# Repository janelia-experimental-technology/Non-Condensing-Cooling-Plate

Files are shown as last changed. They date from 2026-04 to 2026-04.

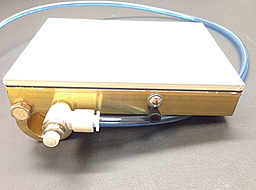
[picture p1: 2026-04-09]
Non-Condensing-Cooling-Plate.png

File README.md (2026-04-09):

### Non-condensing cooling plate

Cooling plates are common in the scientific environment. However, depending on the humidity of the environment, the cold surface of the cooling plate can cause moisture in the air to condense on the surface, thus interfering with certain tasks. For example, if using a cooling plate while sorting fruit flies, excess moisture on the plate may cause flies to drown.

Inventors at Howard Hughes Medical Institute’s Janelia Research Campus have designed a cooling plate that keeps the working surface completely dry and cool, independent of the working environment’s conditions. This is achieved by cooling/drying air and forcing it through a porous stainless steel plate. Instead of water condensing on top of the surface, water is allowed to condense inside the device (below the surface) and is forced out by air pressure through a drain. The airflow is gentle enough not to disturb the work surface, but enough to prevent condensation.

Compressed lab air, a chilled water supply, and peltier with controller are required for this technology. The current configuration is designed for fruit fly sorting and thus has an integrated vial chiller to pre-chill the flies before they are sorted. A variety of vial sizes can be accommodated to the existing design via vial adapters. A variety of fittings can be used and the current design includes push-to-connect tubing, which is easy to install.

Advantages:

&#x20;   Variable temperature and airflow for control of your working conditions.

&#x20;   Removable mesh cover is washable or disposable for a continually clean work surface.

&#x20;   Cover can be a variety of colors to contrast with small objects, such as fruit flies, under a microscope.

Applications:

&#x20;   Life science research

&#x20;   Electronics

&#x20;   Pharmaceutical industry

Opportunity: Free to make for Non-Profit Research by downloading the design here. See included hardware license.

Rights and designs available for Commercial License. Janelia makes no endorsements or guarantees of licensee products.

For inquiries, please contact innovation@janelia.hhmi.org and reference this repository.

To cite the designs, please use DOI: https://doi.org/10.25378/janelia.31972878

Supercedes Flintbox ID 2012-037

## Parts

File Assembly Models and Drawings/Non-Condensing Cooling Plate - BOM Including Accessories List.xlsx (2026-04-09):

J001819 NON CONDENSING COOLING PLATE BOM
Item # | Qty | Part Number | Brand | Item | Notes
1 | 1 | LHP-300-CP | TECA | Cooling plate
2 | 1 | SP-300-24 | TECA | Power supply (for the cooling plate)
3 | 1 | TC-3400 | TECA | Temperature control
4 | 1 | 94115K046 | McMaster | Neoprene O-Ring AS568A Dash Number 046, packs of 10
5 | 1 | 51495K117 | McMaster | Nckl-Pltd Brass Push-to-Connect Tube Fitting Adapter for 1/4" Tube OD X 3/8" NPT Male Pipe
6 | 1 | 9833K21 | McMaster | Breather Vent 1/8 NPT Male, 2 Max SCFM, 7/16" Height
7 | 1 | 91099A167 | McMaster | 18-8 SS Flat Undercut Head Phil Machine Screw 4-40 Thread, 1/2" Length, packs of 100
8 | 1 | 94564A045 | McMaster | Nylon Flat Point Socket Set Screw 10-32 Thread, 1/4" Length, packs of 100
9 | 1 | 95868A087 | McMaster | Nylon Socket Head Cap Screw 10-32 Thread, 3/8" Length, Black, packs of 100
10 | 1 | 3883K24 | McMaster | Heat-Sink Compound Silicone-Free, 2 Ounce Tube
11 | 1 | 9066K18 | McMaster | Corrosion-Resistant Air Flow Control Valve with Plastic Valves, 1/4" Tube OD X 1/8 NPT Male
12 | 1 | 7364T74 | McMaster | Corrosion-Resistant Metal Wool, 316 Stainless Steel, Fine Grade, 3-Pad Package
13 | 1 | 57-105 | Genesee | Mesh, Nitex Nylon 30um | Need about 30 sq in / cold plate
14 | 1 | J001813 | Custom | SIMPLE CHILLED AIR SINTERED PLATE
15 | 1 | J001814 | Custom | SIMPLE CHILLED AIR DRAIN PLATE
16 | 1 | J001816 | Custom | SIMPLE CHILLED AIR BASE PLATE
17 | 1 | J001818 | Custom | SIMPLE CHILLED AIR 12mm x 17mm VIAL ADAPTER
18 | 1 | T257P2 | Thermotek | Pt# 0P9T257P20 Thermoelectric Recirculating Chiller | Similar chillers can be used, and multiple cooling plates can be connected to one chiller

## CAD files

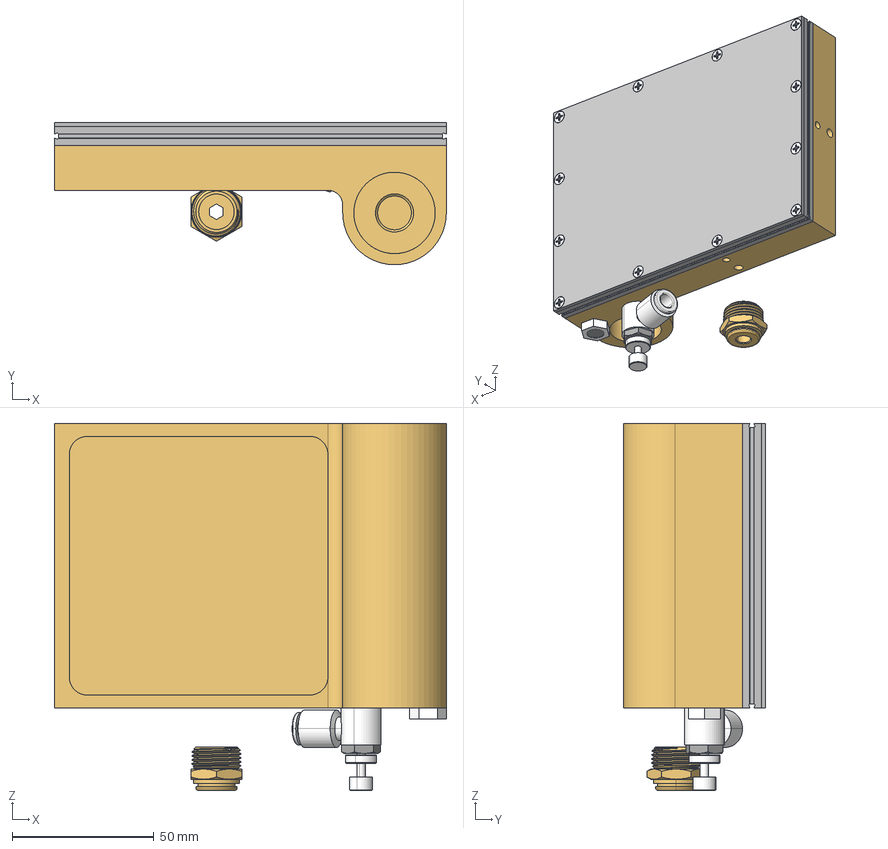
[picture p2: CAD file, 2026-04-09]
Assembly Models and Drawings/SIMPLE CHILLED AIR NON-CONDENSING COOLING PLATE J001819 Rev0.stp
138.2 x 50.2 x 129.4 mm
SIMPLE CHILLED AIR BASE PLATE
SIMPLE CHILLED AIR DRAIN PLATE
SIMPLE CHILLED AIR SINTERED PLATE
91099A167 x 12
SIMPLE CHILLED AIR 12mm X 17mm VIAL ADAPTER
SMC AS2211F-UO1-07
SIMPLE CHILLED AIR WALL FITTING
BREATHER VENT

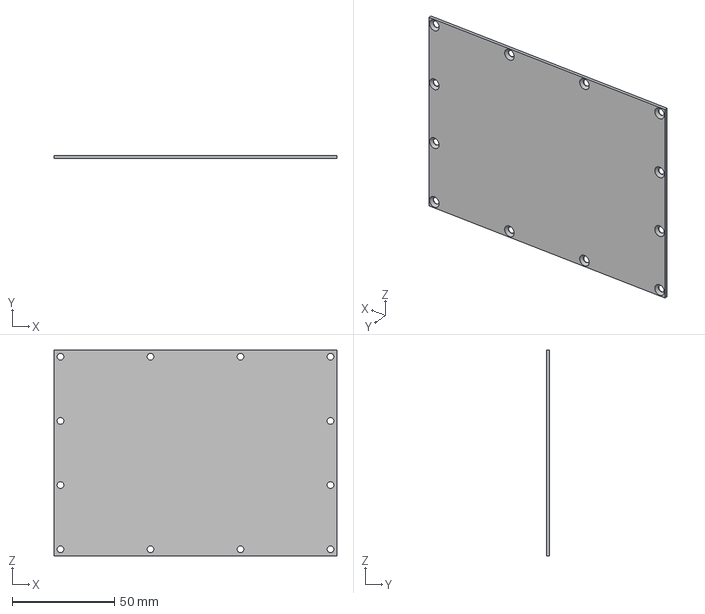
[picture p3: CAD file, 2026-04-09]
Part Models and Drawings/SIMPLE CHILLED AIR SINTERED PLATE J001813 Rev -.stp
138.1 x 1.57 x 100.3 mm

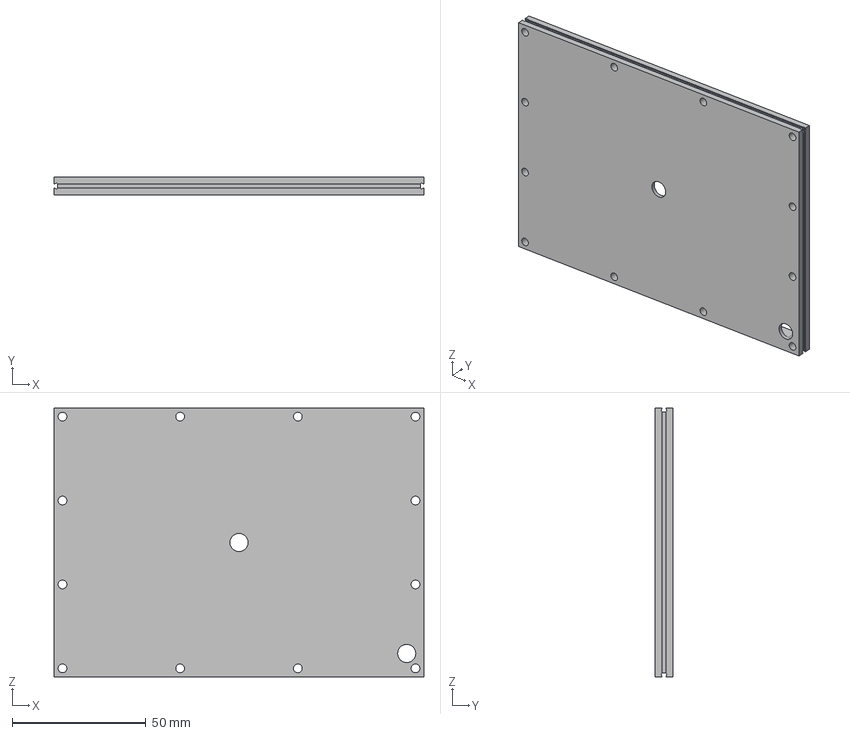
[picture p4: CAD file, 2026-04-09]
Part Models and Drawings/SIMPLE CHILLED AIR DRAIN PLATE J001814 Rev -.stp
138.1 x 6.58 x 100.3 mm

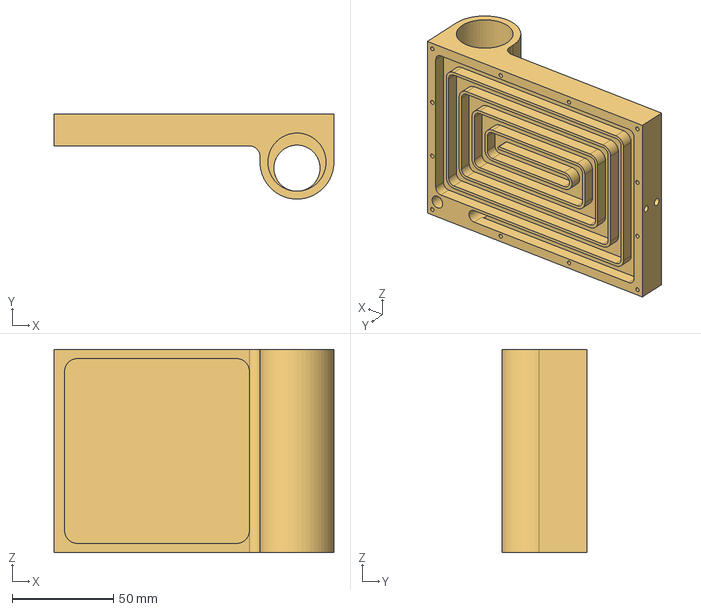
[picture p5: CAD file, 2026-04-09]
Part Models and Drawings/SIMPLE CHILLED AIR BASE PLATE J001816 Rev -.stp
138.1 x 42.1 x 100.3 mm

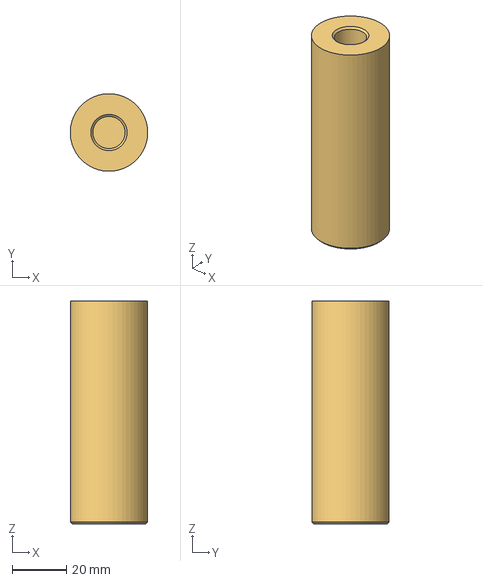
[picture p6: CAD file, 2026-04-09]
Part Models and Drawings/SIMPLE CHILLED AIR 12mm X 17mm VIAL ADAPTER J001818 Rev -.stp
28.7 x 28.7 x 82.5 mm

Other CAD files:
Inventor Pack and Go/91099A167.ipt
Inventor Pack and Go/BREATHER VENT.ipt
Inventor Pack and Go/SIMPLE CHILLED AIR 12mm X 17mm VIAL ADAPTER.ipt
Inventor Pack and Go/SIMPLE CHILLED AIR BASE PLATE.ipt
Inventor Pack and Go/SIMPLE CHILLED AIR DRAIN PLATE.ipt
Inventor Pack and Go/SIMPLE CHILLED AIR NON-CONDENSING COOLING PLATE.iam
Inventor Pack and Go/SIMPLE CHILLED AIR SINTERED PLATE.ipt
Inventor Pack and Go/SIMPLE CHILLED AIR WALL FITTING.ipt
Inventor Pack and Go/SMC AS2211F-UO1-07.ipt
Inventor Pack and Go/_SIMPLE CHILLED AIR COOLING PLATE.ipt

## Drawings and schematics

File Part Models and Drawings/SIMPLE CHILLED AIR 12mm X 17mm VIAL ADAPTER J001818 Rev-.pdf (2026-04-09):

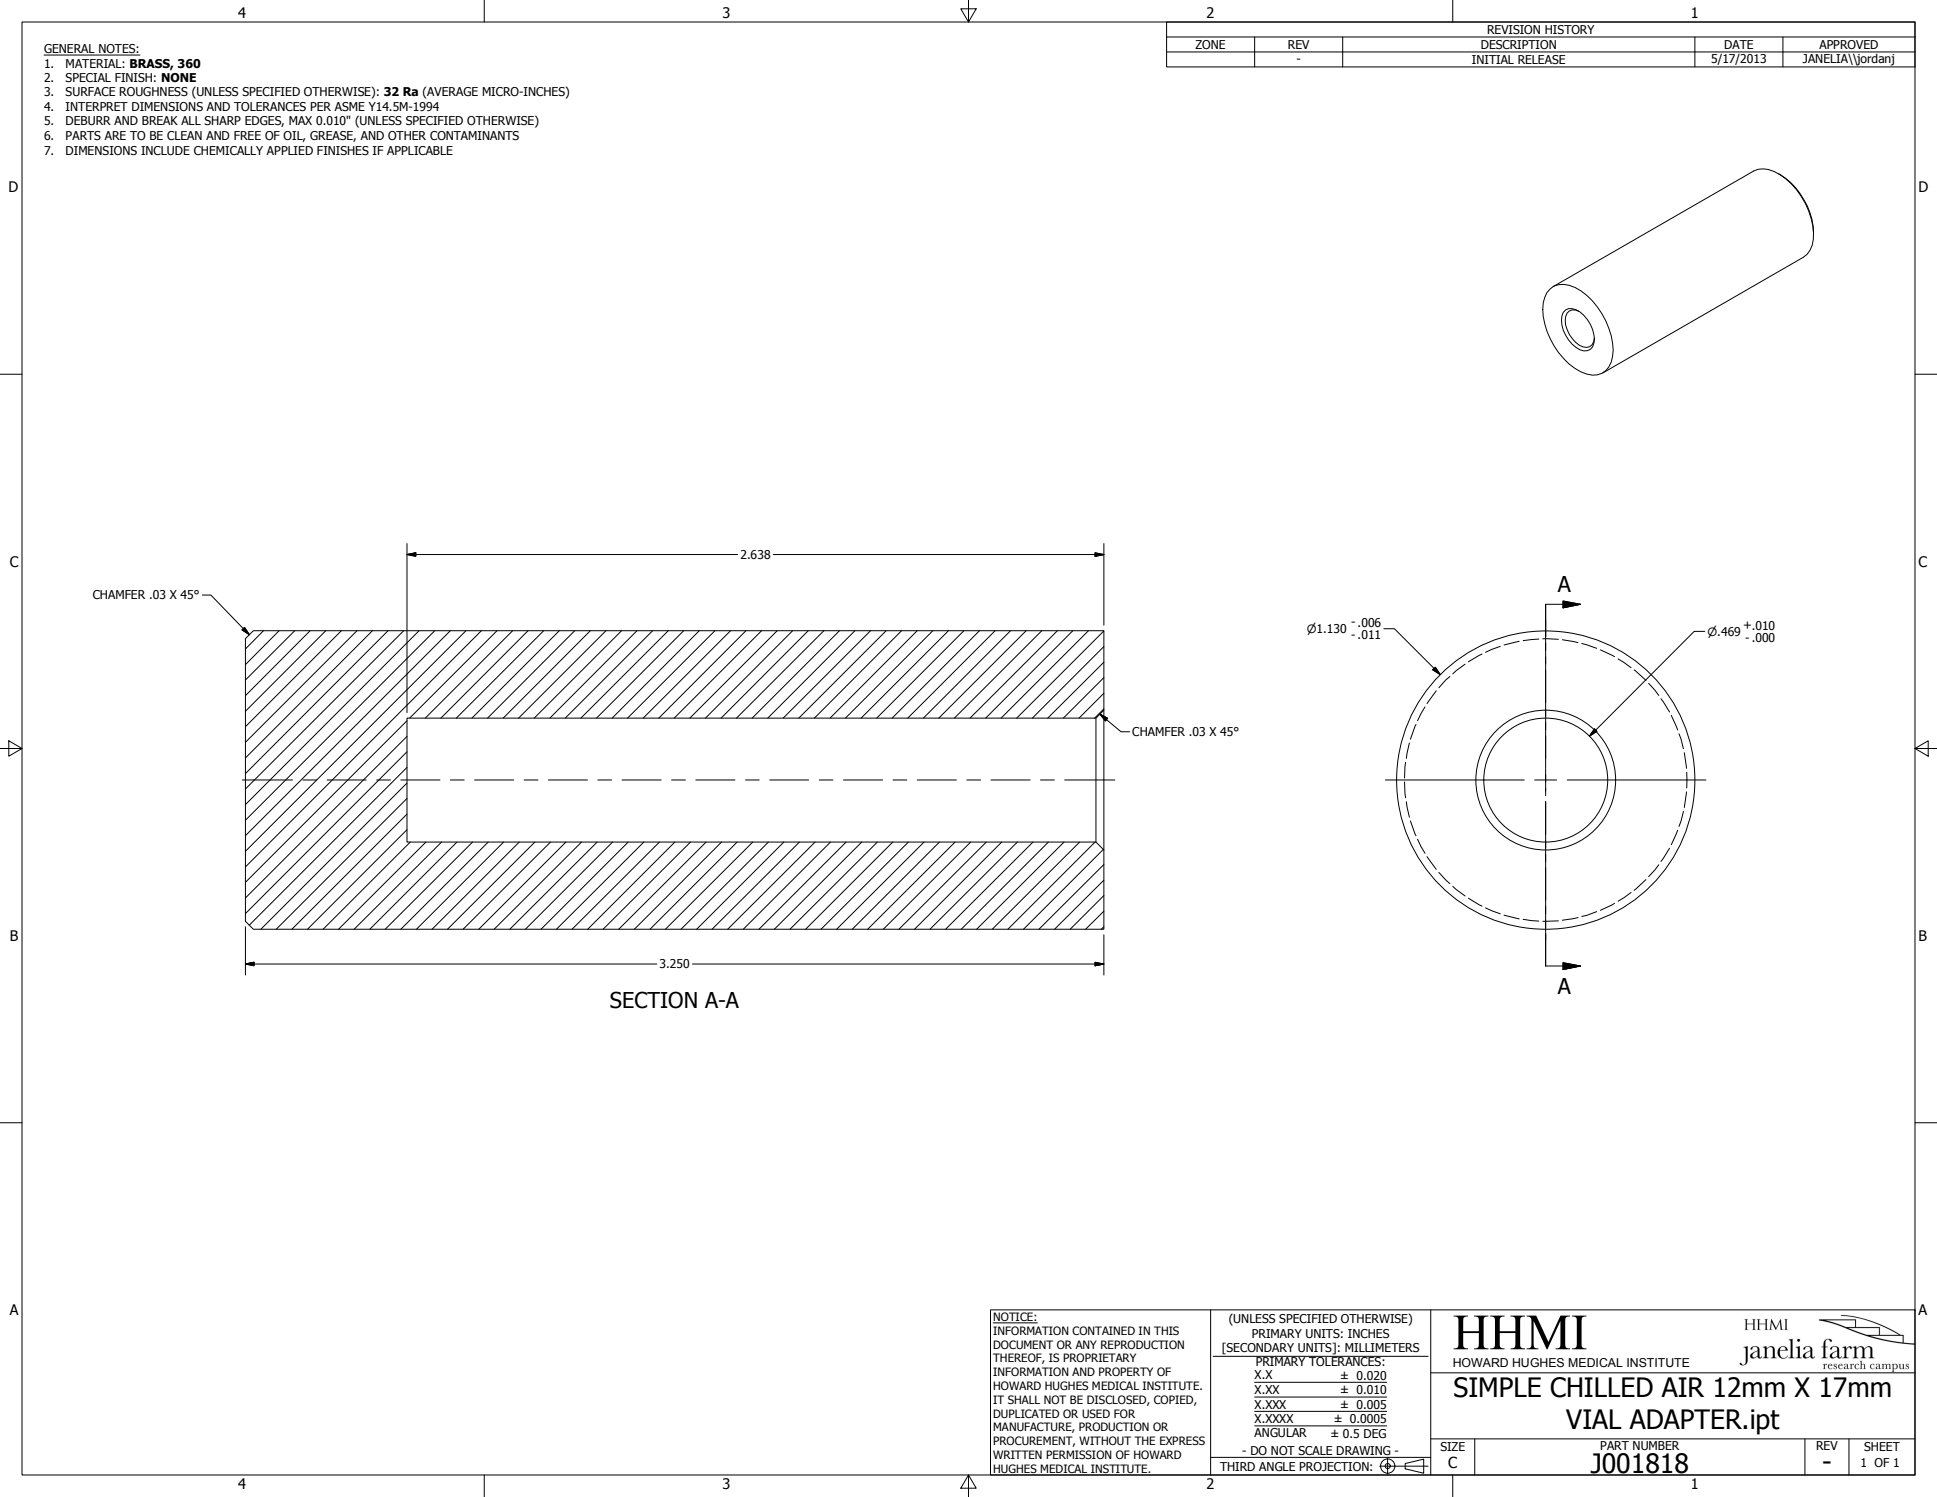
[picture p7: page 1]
SECTION A-A; PART NUMBER; HHMI; SIZE; REV; SHEET; 1 OF 1 THIRD ANGLE PROJECTION:; ± 0.020 ± 0.010 ± 0.005 ± 0.0005 ± 0.5 DEG; REVISION HISTORY; ZONE; DESCRIPTION; DATE; APPROVED; INITIAL RELEASE; JANELIA\\jordanj; CHAMFER .03 X 45°

GENERAL NOTES:
1. MATERIAL: BRASS, 360
2. SPECIAL FINISH: NONE
3. SURFACE ROUGHNESS (UNLESS SPECIFIED OTHERWISE): 32 Ra (AVERAGE MICRO-INCHES)
4. INTERPRET DIMENSIONS AND TOLERANCES PER ASME Y14.5M-1994
5. DEBURR AND BREAK ALL SHARP EDGES, MAX 0.010" (UNLESS SPECIFIED OTHERWISE)
6. PARTS ARE TO BE CLEAN AND FREE OF OIL, GREASE, AND OTHER CONTAMINANTS
7. DIMENSIONS INCLUDE CHEMICALLY APPLIED FINISHES IF APPLICABLE

NOTICE:
INFORMATION CONTAINED IN THIS
DOCUMENT OR ANY REPRODUCTION
THEREOF, IS PROPRIETARY
INFORMATION AND PROPERTY OF
HOWARD HUGHES MEDICAL INSTITUTE.
IT SHALL NOT BE DISCLOSED, COPIED,
DUPLICATED OR USED FOR
MANUFACTURE, PRODUCTION OR
PROCUREMENT, WITHOUT THE EXPRESS
WRITTEN PERMISSION OF HOWARD
HUGHES MEDICAL INSTITUTE.

(UNLESS SPECIFIED OTHERWISE)
PRIMARY UNITS: INCHES
[SECONDARY UNITS]: MILLIMETERS
PRIMARY TOLERANCES:
X.XXX
X.XXXX
ANGULAR
- DO NOT SCALE DRAWING -

HOWARD HUGHES MEDICAL INSTITUTE
SIMPLE CHILLED AIR 12mm X 17mm

VIAL ADAPTER.ipt

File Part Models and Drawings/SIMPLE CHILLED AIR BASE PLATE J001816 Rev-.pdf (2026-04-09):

B

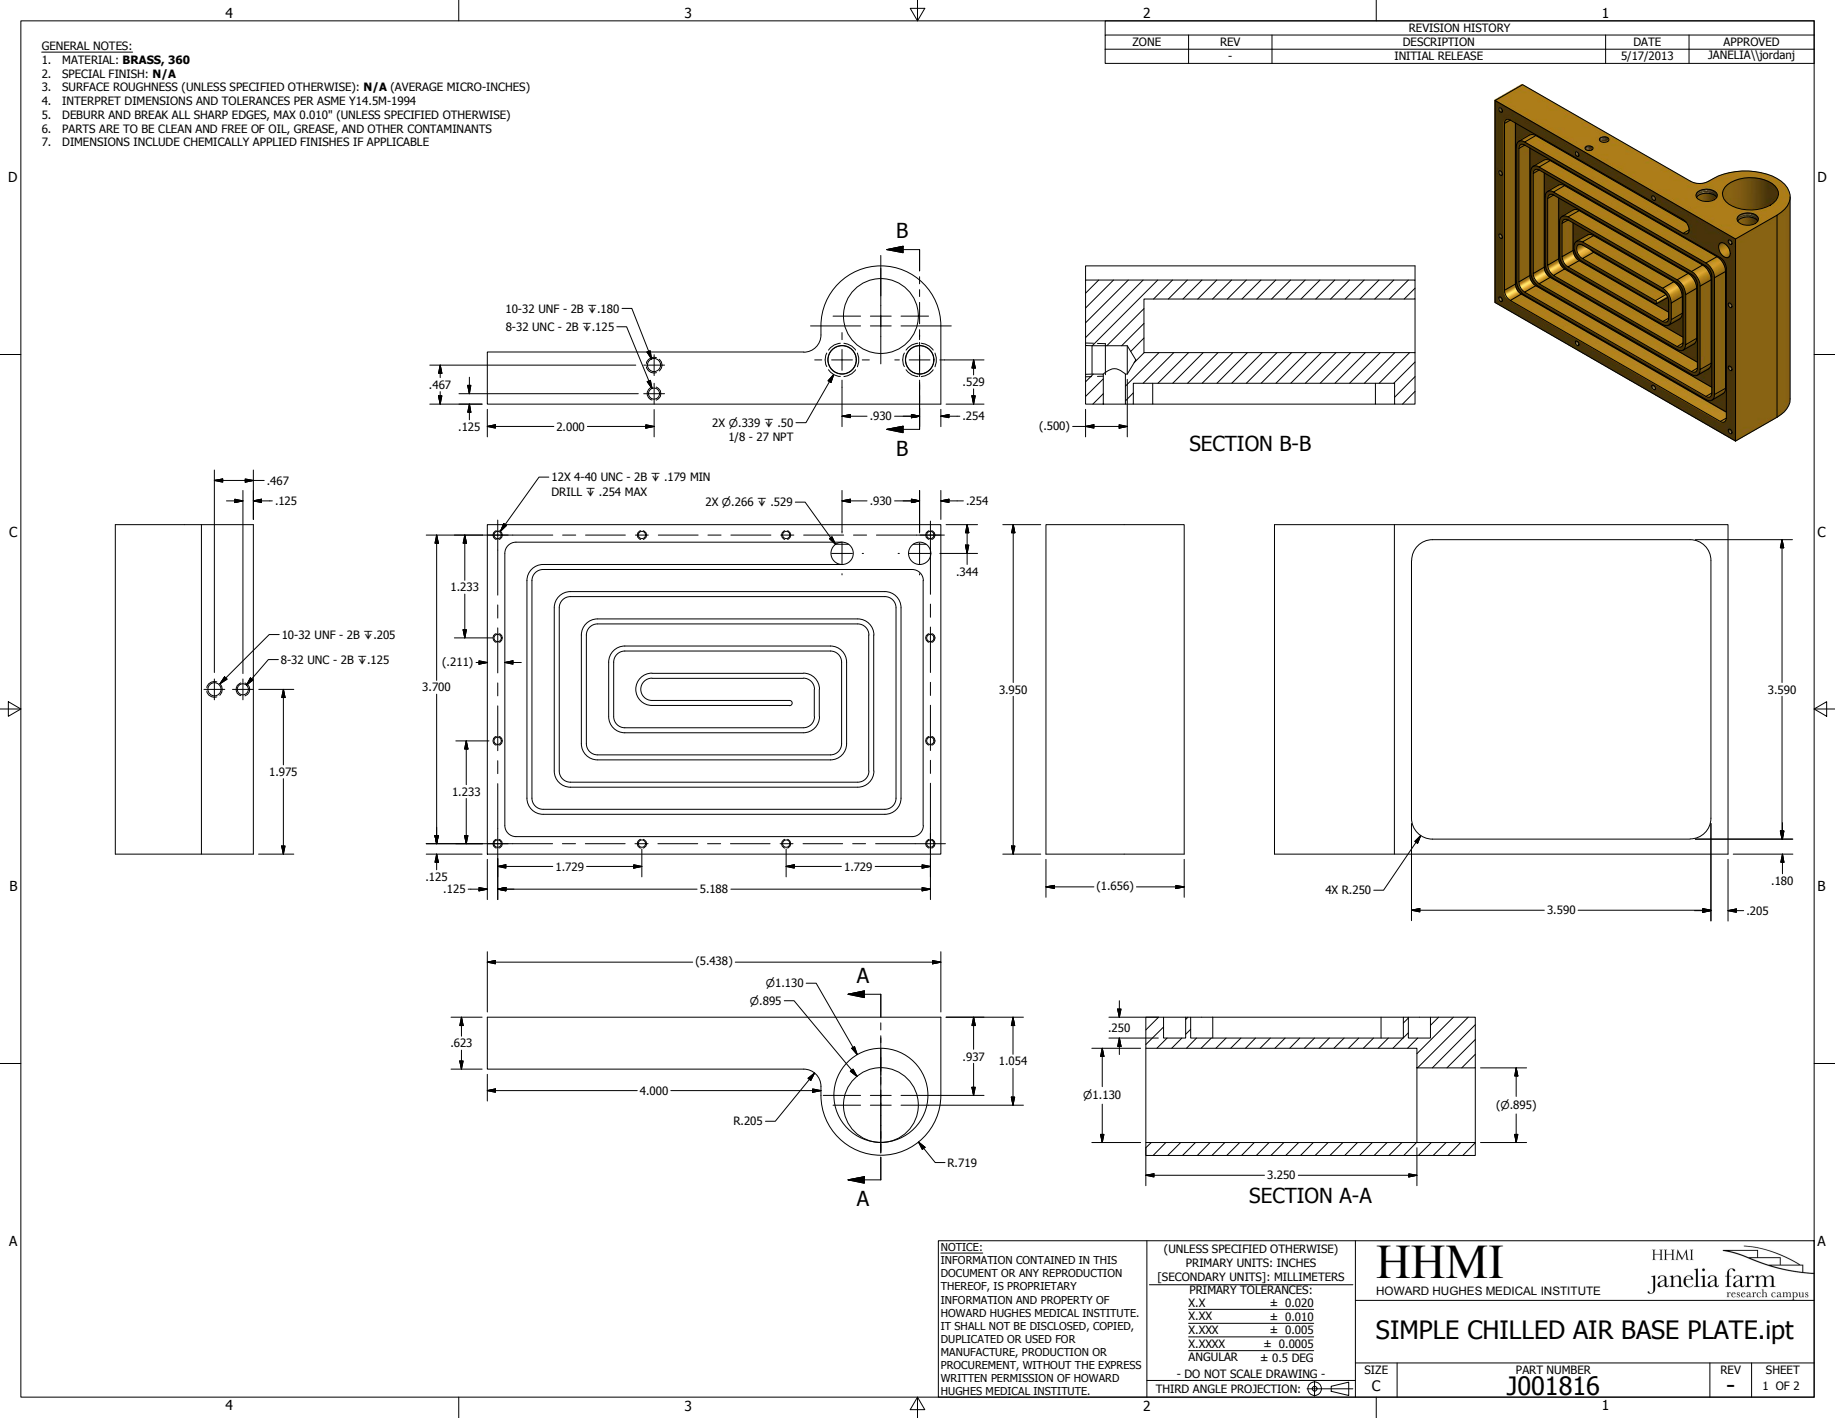
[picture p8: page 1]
SECTION A-A; SECTION B-B; PART NUMBER; HHMI; SIZE; REV; SHEET; 1 OF 2 THIRD ANGLE PROJECTION:; ± 0.020 ± 0.010 ± 0.005 ± 0.0005 ± 0.5 DEG; REVISION HISTORY; ZONE; DESCRIPTION; DATE; APPROVED; INITIAL RELEASE; JANELIA\\jordanj; 12X 4-40 UNC - 2B Z .179 MIN DRILL Z .254 MAX; 8-32 UNC - 2B Z.125; 10-32 UNF - 2B Z.205; 10-32 UNF - 2B Z.180; 1/8 - 27 NPT

GENERAL NOTES:
1. MATERIAL: BRASS, 360
2. SPECIAL FINISH: N/A
3. SURFACE ROUGHNESS (UNLESS SPECIFIED OTHERWISE): N/A (AVERAGE MICRO-INCHES)
4. INTERPRET DIMENSIONS AND TOLERANCES PER ASME Y14.5M-1994
5. DEBURR AND BREAK ALL SHARP EDGES, MAX 0.010" (UNLESS SPECIFIED OTHERWISE)
6. PARTS ARE TO BE CLEAN AND FREE OF OIL, GREASE, AND OTHER CONTAMINANTS
7. DIMENSIONS INCLUDE CHEMICALLY APPLIED FINISHES IF APPLICABLE

NOTICE:
INFORMATION CONTAINED IN THIS
DOCUMENT OR ANY REPRODUCTION
THEREOF, IS PROPRIETARY
INFORMATION AND PROPERTY OF
HOWARD HUGHES MEDICAL INSTITUTE.
IT SHALL NOT BE DISCLOSED, COPIED,
DUPLICATED OR USED FOR
MANUFACTURE, PRODUCTION OR
PROCUREMENT, WITHOUT THE EXPRESS
WRITTEN PERMISSION OF HOWARD
HUGHES MEDICAL INSTITUTE.

(UNLESS SPECIFIED OTHERWISE)
PRIMARY UNITS: INCHES
[SECONDARY UNITS]: MILLIMETERS
PRIMARY TOLERANCES:
X.XXX
X.XXXX
ANGULAR
- DO NOT SCALE DRAWING -

HOWARD HUGHES MEDICAL INSTITUTE
SIMPLE CHILLED AIR BASE PLATE.ipt

C

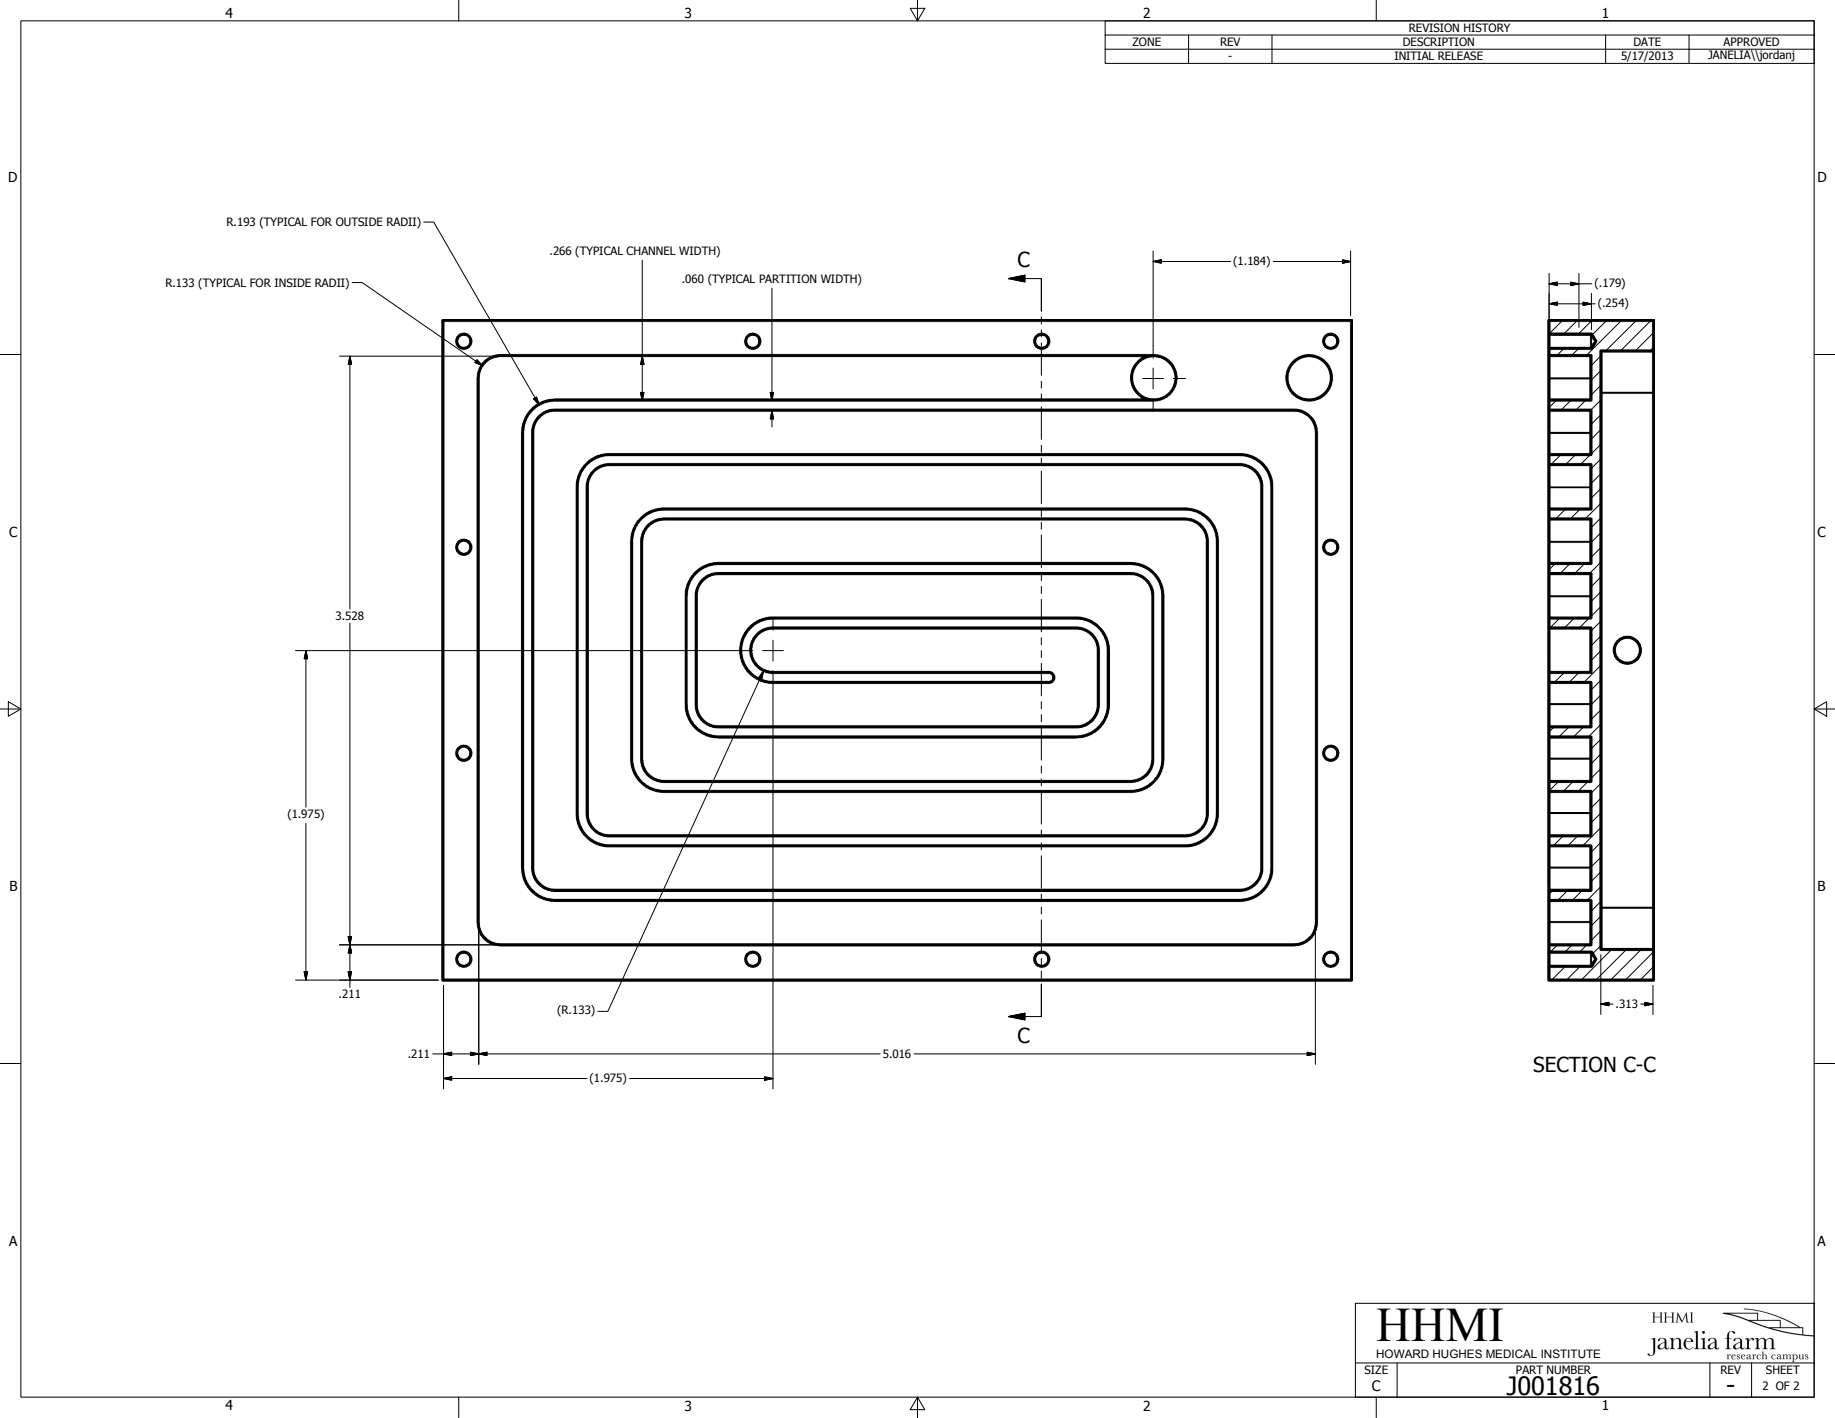
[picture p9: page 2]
SECTION C-C; PART NUMBER; HHMI; SIZE; REV; SHEET; REVISION HISTORY; ZONE; DESCRIPTION; DATE; APPROVED; INITIAL RELEASE; JANELIA\\jordanj

R.193 (TYPICAL FOR OUTSIDE RADII)

.266 (TYPICAL CHANNEL WIDTH)

R.133 (TYPICAL FOR INSIDE RADII)

.060 (TYPICAL PARTITION WIDTH)

HOWARD HUGHES MEDICAL INSTITUTE

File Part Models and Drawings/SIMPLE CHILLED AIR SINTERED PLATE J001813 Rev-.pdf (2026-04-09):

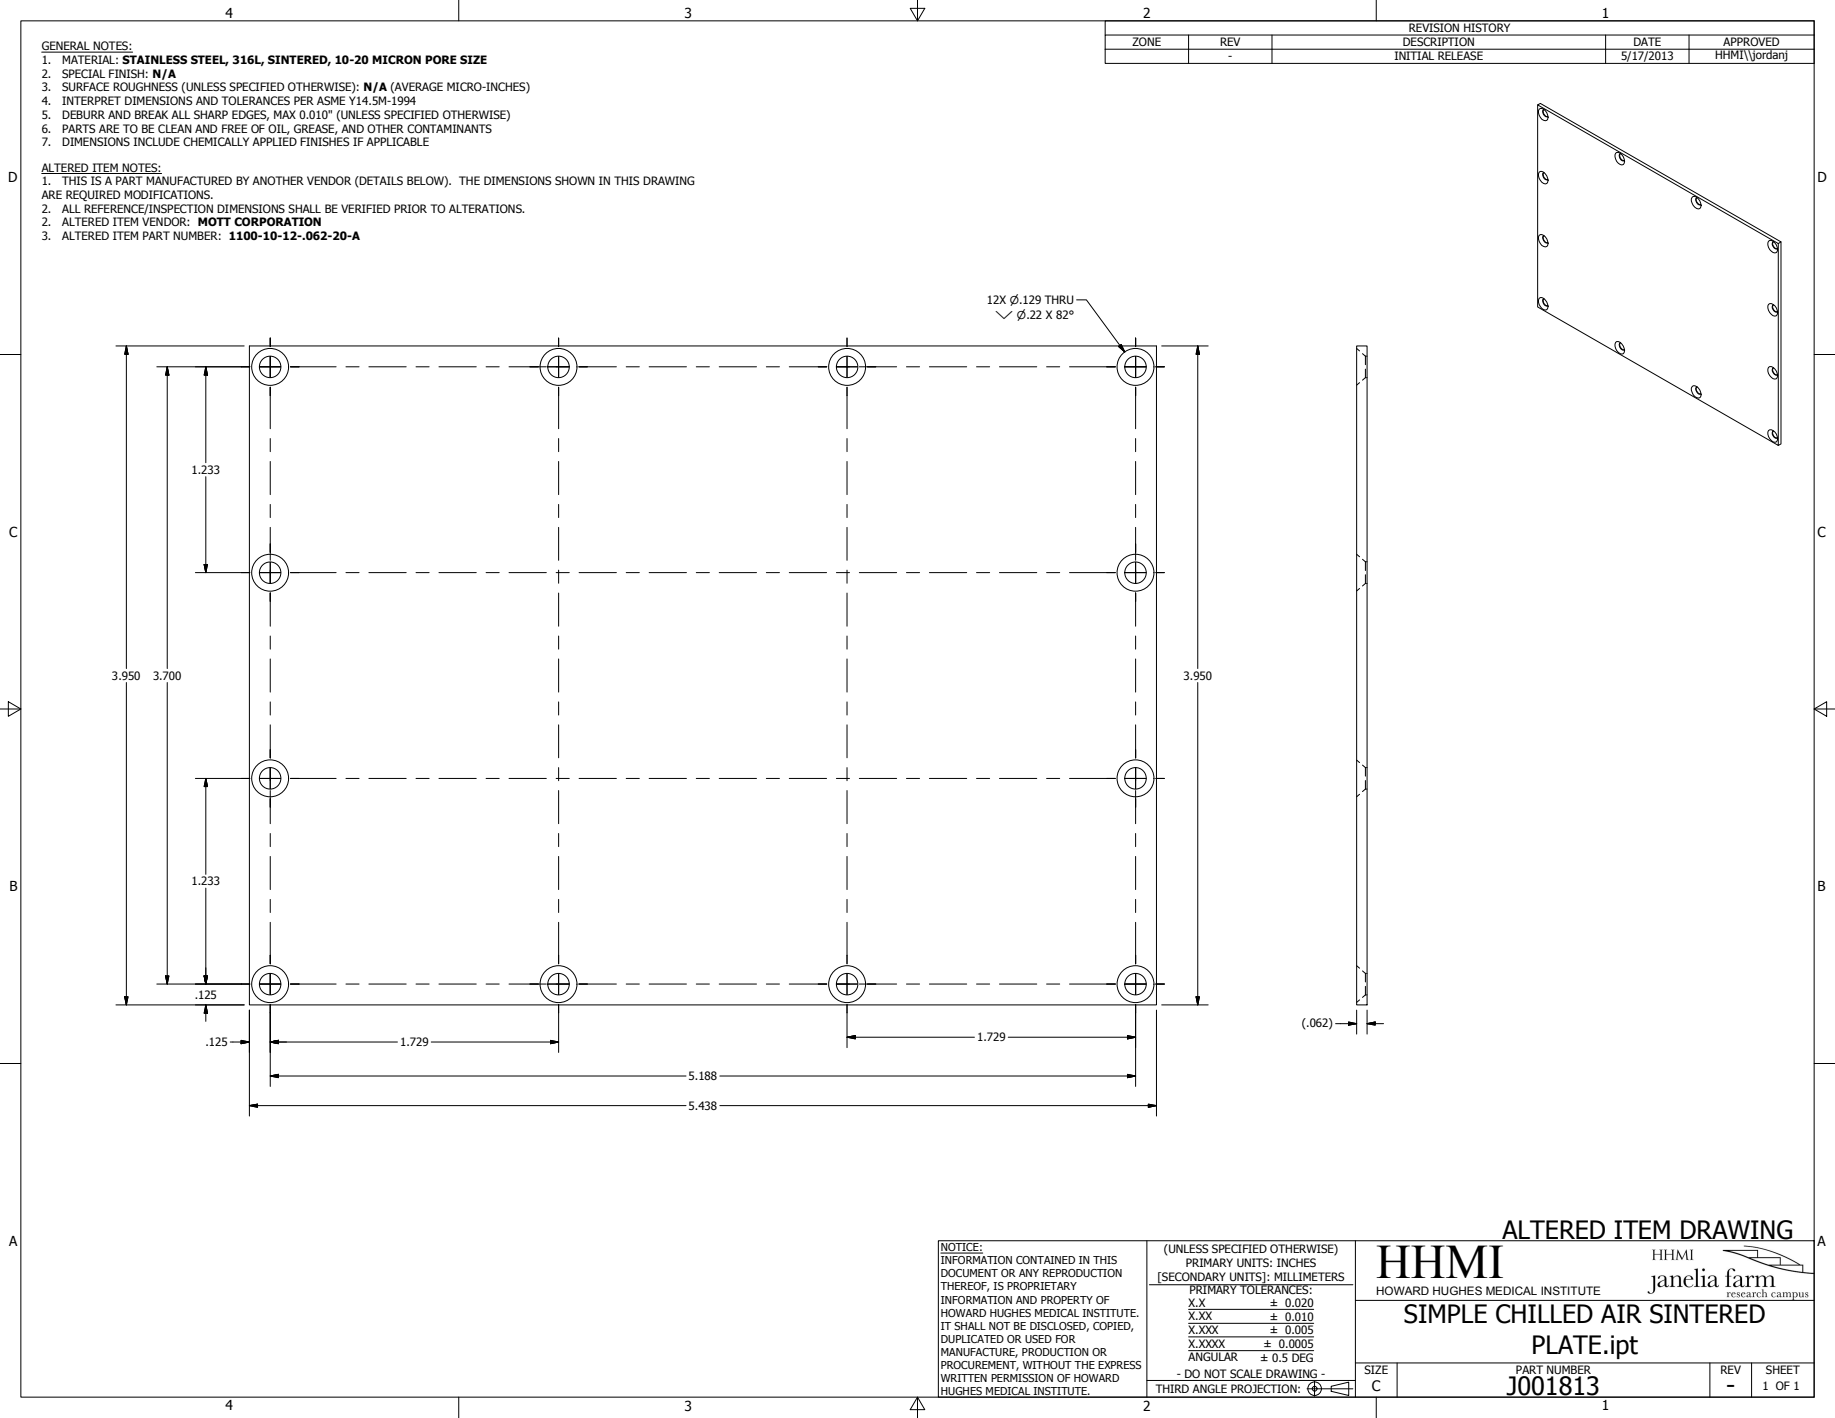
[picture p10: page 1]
PART NUMBER; SIZE; REV; SHEET; 1 OF 1 THIRD ANGLE PROJECTION:; ± 0.020 ± 0.010 ± 0.005 ± 0.0005 ± 0.5 DEG; PLATE.ipt; REVISION HISTORY; ZONE; DESCRIPTION; DATE; APPROVED; INITIAL RELEASE; HHMI\\jordanj; 12X P.129 THRU Y P.22 X 82°

GENERAL NOTES:
1. MATERIAL: STAINLESS STEEL, 316L, SINTERED, 10-20 MICRON PORE SIZE
2. SPECIAL FINISH: N/A
3. SURFACE ROUGHNESS (UNLESS SPECIFIED OTHERWISE): N/A (AVERAGE MICRO-INCHES)
4. INTERPRET DIMENSIONS AND TOLERANCES PER ASME Y14.5M-1994
5. DEBURR AND BREAK ALL SHARP EDGES, MAX 0.010" (UNLESS SPECIFIED OTHERWISE)
6. PARTS ARE TO BE CLEAN AND FREE OF OIL, GREASE, AND OTHER CONTAMINANTS
7. DIMENSIONS INCLUDE CHEMICALLY APPLIED FINISHES IF APPLICABLE

ALTERED ITEM NOTES:

1. THIS IS A PART MANUFACTURED BY ANOTHER VENDOR (DETAILS BELOW). THE DIMENSIONS SHOWN IN THIS DRAWING
ARE REQUIRED MODIFICATIONS.
2. ALL REFERENCE/INSPECTION DIMENSIONS SHALL BE VERIFIED PRIOR TO ALTERATIONS.
2. ALTERED ITEM VENDOR: MOTT CORPORATION
3. ALTERED ITEM PART NUMBER: 1100-10-12-.062-20-A

ALTERED ITEM DRAWING
HHMI

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

HOWARD HUGHES MEDICAL INSTITUTE
SIMPLE CHILLED AIR SINTERED

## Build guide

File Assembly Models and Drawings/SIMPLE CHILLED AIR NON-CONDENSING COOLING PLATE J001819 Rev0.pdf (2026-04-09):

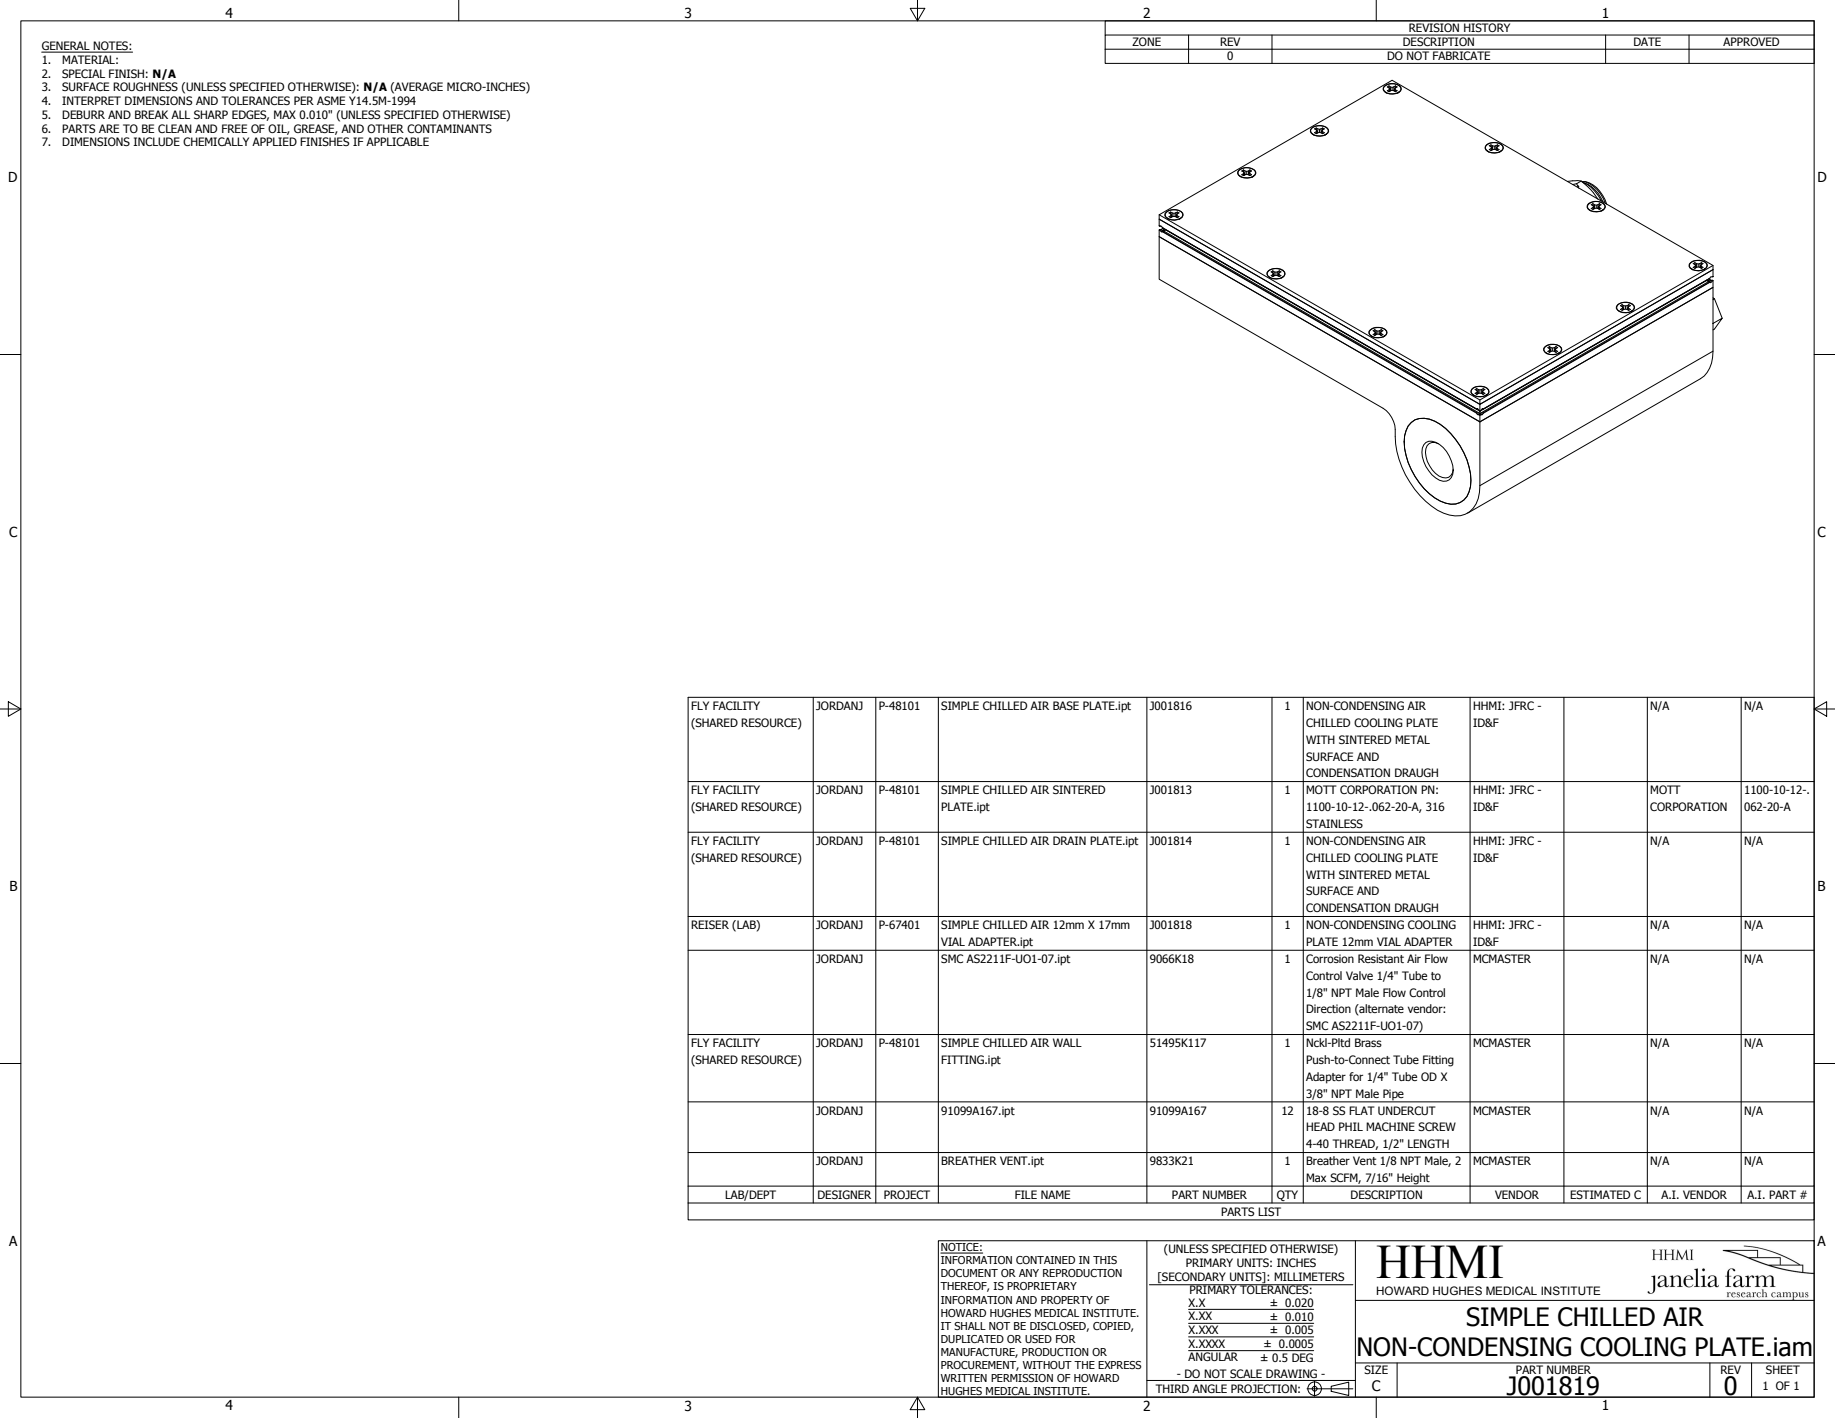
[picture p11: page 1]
Breather Vent 1/8 NPT Male, 2; MCMASTER; JORDANJ; BREATHER VENT.ipt; PARTS LIST; LAB/DEPT; DESIGNER; PROJECT; FILE NAME; PART NUMBER; QTY; DESCRIPTION; VENDOR; ESTIMATED C; A.I. VENDOR; A.I. PART #; SIZE; REV; SHEET; 1 OF 1 THIRD ANGLE PROJECTION:; ± 0.020 ± 0.010 ± 0.005 ± 0.0005 ± 0.5 DEG; REVISION HISTORY; ZONE; DATE; APPROVED; DO NOT FABRICATE

GENERAL NOTES:
1. MATERIAL:
2. SPECIAL FINISH: N/A
3. SURFACE ROUGHNESS (UNLESS SPECIFIED OTHERWISE): N/A (AVERAGE MICRO-INCHES)
4. INTERPRET DIMENSIONS AND TOLERANCES PER ASME Y14.5M-1994
5. DEBURR AND BREAK ALL SHARP EDGES, MAX 0.010" (UNLESS SPECIFIED OTHERWISE)
6. PARTS ARE TO BE CLEAN AND FREE OF OIL, GREASE, AND OTHER CONTAMINANTS
7. DIMENSIONS INCLUDE CHEMICALLY APPLIED FINISHES IF APPLICABLE

FLY FACILITY (SHARED RESOURCE) | JORDANJ | P-48101 | SIMPLE CHILLED AIR BASE PLATE.ipt | J001816 | 1 | NON-CONDENSING AIR CHILLED COOLING PLATE WITH SINTERED METAL SURFACE AND CONDENSATION DRAUGH | HHMI: JFRC -ID&F | N/A | N/A

FLY FACILITY (SHARED RESOURCE) | JORDANJ | P-48101 | SIMPLE CHILLED AIR SINTERED PLATE.ipt | J001813 | 1 | MOTT CORPORATION PN: 1100-10-12-.062-20-A, 316 STAINLESS | HHMI: JFRC -ID&F | MOTT CORPORATION | 1100-10-12-. 062-20-A

FLY FACILITY (SHARED RESOURCE) | JORDANJ | P-48101 | SIMPLE CHILLED AIR DRAIN PLATE.ipt | J001814 | 1 | NON-CONDENSING AIR CHILLED COOLING PLATE WITH SINTERED METAL SURFACE AND CONDENSATION DRAUGH | HHMI: JFRC -ID&F | N/A | N/A

REISER (LAB) | JORDANJ | P-67401 | SIMPLE CHILLED AIR 12mm X 17mm VIAL ADAPTER.ipt | J001818 | 1 | NON-CONDENSING COOLING PLATE 12mm VIAL ADAPTER | HHMI: JFRC -ID&F | N/A | N/A

JORDANJ | | SMC AS2211F-UO1-07.ipt | 9066K18 | 1 | Corrosion Resistant Air Flow Control Valve 1/4" Tube to 1/8" NPT Male Flow Control Direction (alternate vendor: SMC AS2211F-UO1-07) | MCMASTER | N/A | N/A

FLY FACILITY (SHARED RESOURCE) | JORDANJ | P-48101 | SIMPLE CHILLED AIR WALL FITTING.ipt | 51495K117 | 1 | Nckl-Pltd Brass Push-to-Connect Tube Fitting Adapter for 1/4" Tube OD X 3/8" NPT Male Pipe | MCMASTER | N/A | N/A

JORDANJ | | 91099A167.ipt | 91099A167 | 12 | 18-8 SS FLAT UNDERCUT HEAD PHIL MACHINE SCREW 4-40 THREAD, 1/2" LENGTH | MCMASTER | N/A | N/A

Max SCFM, 7/16" Height
HHMI

NOTICE:
INFORMATION CONTAINED IN THIS
DOCUMENT OR ANY REPRODUCTION
THEREOF, IS PROPRIETARY
INFORMATION AND PROPERTY OF
HOWARD HUGHES MEDICAL INSTITUTE.
IT SHALL NOT BE DISCLOSED, COPIED,
DUPLICATED OR USED FOR
MANUFACTURE, PRODUCTION OR
PROCUREMENT, WITHOUT THE EXPRESS
WRITTEN PERMISSION OF HOWARD
HUGHES MEDICAL INSTITUTE.

(UNLESS SPECIFIED OTHERWISE)
PRIMARY UNITS: INCHES
[SECONDARY UNITS]: MILLIMETERS
PRIMARY TOLERANCES:
X.XXX
X.XXXX
ANGULAR
- DO NOT SCALE DRAWING -

HOWARD HUGHES MEDICAL INSTITUTE

SIMPLE CHILLED AIR

NON-CONDENSING COOLING PLATE.iam
